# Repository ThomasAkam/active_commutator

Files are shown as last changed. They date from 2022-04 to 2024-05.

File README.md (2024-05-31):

# Active commutator

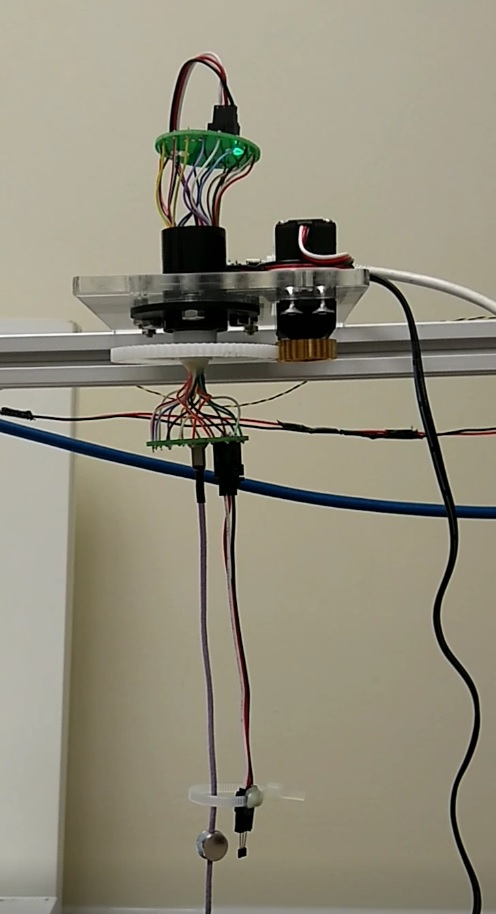
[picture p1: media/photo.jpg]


A simple open source active commutator for Open Ephys / Intan electrophysiology systems.  Uses a hall sensor and magnet to detect rotation of the cable,  a slip ring powered by a continuous rotation servo to correct it, controlled by an Adafruit Trinket M0  running Circuitpython. 

Inspired by earlier designs from [Liberti et al. 2017](https://iopscience.iop.org/article/10.1088/1741-2552/aa6806/meta) and [Fee and Leonardo 2001](https://www.sciencedirect.com/science/article/pii/S0165027001004265).

## Wiring diagram

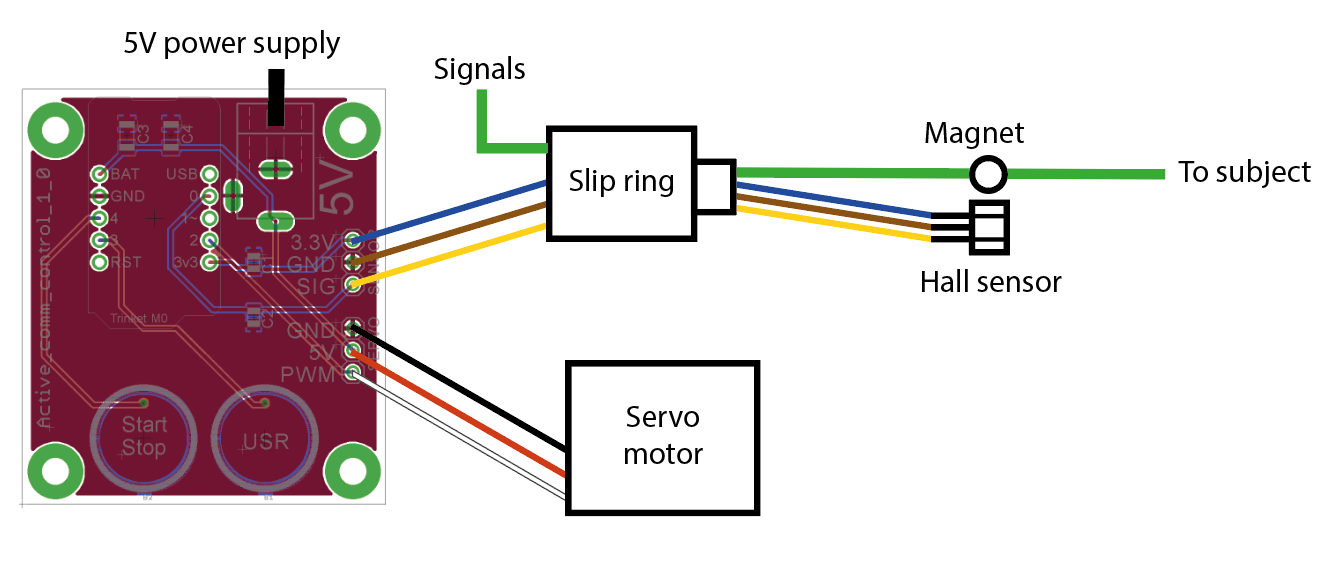
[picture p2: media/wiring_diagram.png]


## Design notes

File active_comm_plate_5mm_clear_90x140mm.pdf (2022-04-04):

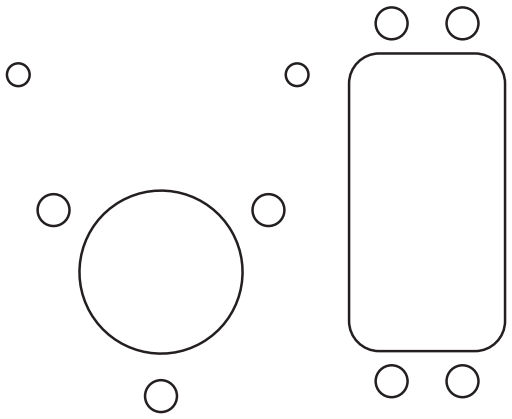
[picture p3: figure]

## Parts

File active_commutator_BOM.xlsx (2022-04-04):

Part | Quantity | Manufacturer | Supplier | Part number | Notes
Mechanical components
Parallax continuous rotation servo (25T/3F spline) | 1 | Parallax | RS | 781-3046 | https://uk.rs-online.com/web/p/servo-motors/7813046
Spur gear mod 0.8, 70 teeth, 6mm bore | 1 | RS | RS | 521-7427 | https://uk.rs-online.com/web/p/spur-gears/5217427/
32P, 24 teeth, 25T/3F Spline, Servo Mount Gear (Metal) | 1 | Servocity | Active Robots | 615306 | https://www.active-robots.com/32p-25t-3f-spline-servo-mount-gears-metal.html
Neodymium magnet 10mm x 1mm | 4 |  | First4Magnets | F307-20 | https://www.first4magnets.com/circular-disc-rod-c34/10mm-dia-x-1mm-thick-n42-neodymium-magnet-0-58kg-pull-p2818|ps_1_936
M4 12mm countersunk screw | 7
M4 Nut | 7
M3 12mm cap head screw | 4
M3 3mm spacer | 4
M3 Nut | 4
Acrylic plate | 1 |  |  |  | Laser cut in 5mm clear acrylic from file active_comm_plate_5mm_clear_90x140mm.dxf
Electrical components
18 wire slip ring | 1 | Senring | Senring | M220-A-18 | https://www.senring.com/capsule-slip-ring/m220.html
Hall sensor 3.3V | 1 | Allegro Microsystems | RS | A1319LUA-5-T | https://uk.rs-online.com/web/p/hall-effect-sensor-ics/8660758/
Phidget Cable 10cm (Molex SL 3 way) | 2 |  | Active Robots |  | https://www.active-robots.com/3003-phidget-cable-10cm.html
active_comm_connector PCB | 2 |  |  |  | Fabricate from Gerbers in folder PCB/active_comm_connector/gerber
active_comm_controller PCB | 1 |  |  |  | Fabricate from Gerbers in folder PCB/active_comm_controller/gerber
5V power supply, 2.1mm barrel plug | 1 | RS | RS | 175-3292 | https://uk.rs-online.com/web/p/ac-dc-adapters/1753292/
Trinket-M0 | 1 | Adafruit | CPC Farnell | SC15313 | Used on active_comm_controller PCB
Pin header 5 way | 2 | Molex | Farnell | 3049532 | Used on active_comm_controller PCB
Receptacle 5 way | 2 | Multicomp | Farnell | 1593461 | Used on active_comm_controller PCB
Pin header 3 way | 1 | Molex | Farnell | 3049527 | Used on active_comm_controller PCB
Capacitor 100nF 0805 | 1 | Multicomp | Farnell | 1759143 | Used on active_comm_controller PCB
Capacitor 4.7nF 0805 | 1 | Multicomp | Farnell | 1759241 | Used on active_comm_controller PCB
Capacitor 220uF 1206 | 2 | Murata | Farnell | 2494472 | Used on active_comm_controller PCB
2.1mm socket | 1 | Lumberg | Farnell | 1217037 | Used on active_comm_controller PCB
Molex SL 3 way header | 3 | Molex | Farnell | 2679892 | Used on active_comm_controller and active_comm_connector PCBs
PZN-12-VV connector | 2 | Omnetics | Genalog |  | Used on active_comm_connector PCB

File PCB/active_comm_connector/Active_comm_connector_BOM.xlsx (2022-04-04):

Part | Value | Device | Package | Description | MF | MPN | OC_FARNELL
PZN-12-VV | - | - | - | Connector | Omnetics | PZN-12-VV

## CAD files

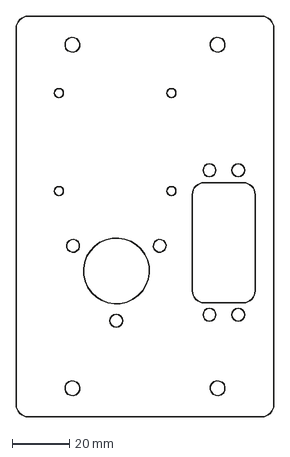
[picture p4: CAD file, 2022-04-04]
active_comm_plate_5mm_clear_90x140mm.dxf
90.0 x 140.0 mm

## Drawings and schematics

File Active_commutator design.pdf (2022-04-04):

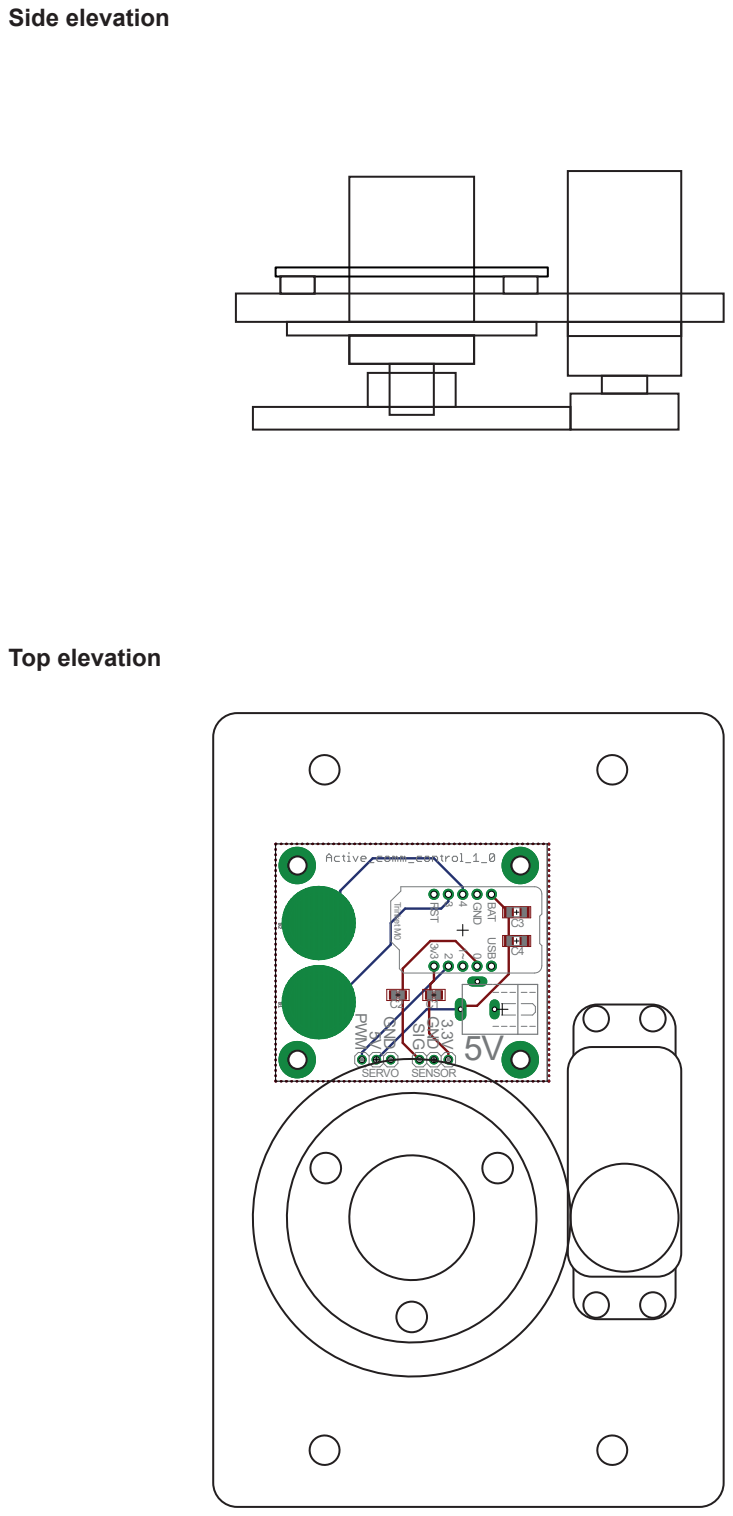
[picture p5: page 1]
Side elevation; GND SIG; GND; Trinket M0; BAT GND; SERVO SENSOR; Top elevation

Start Stop US

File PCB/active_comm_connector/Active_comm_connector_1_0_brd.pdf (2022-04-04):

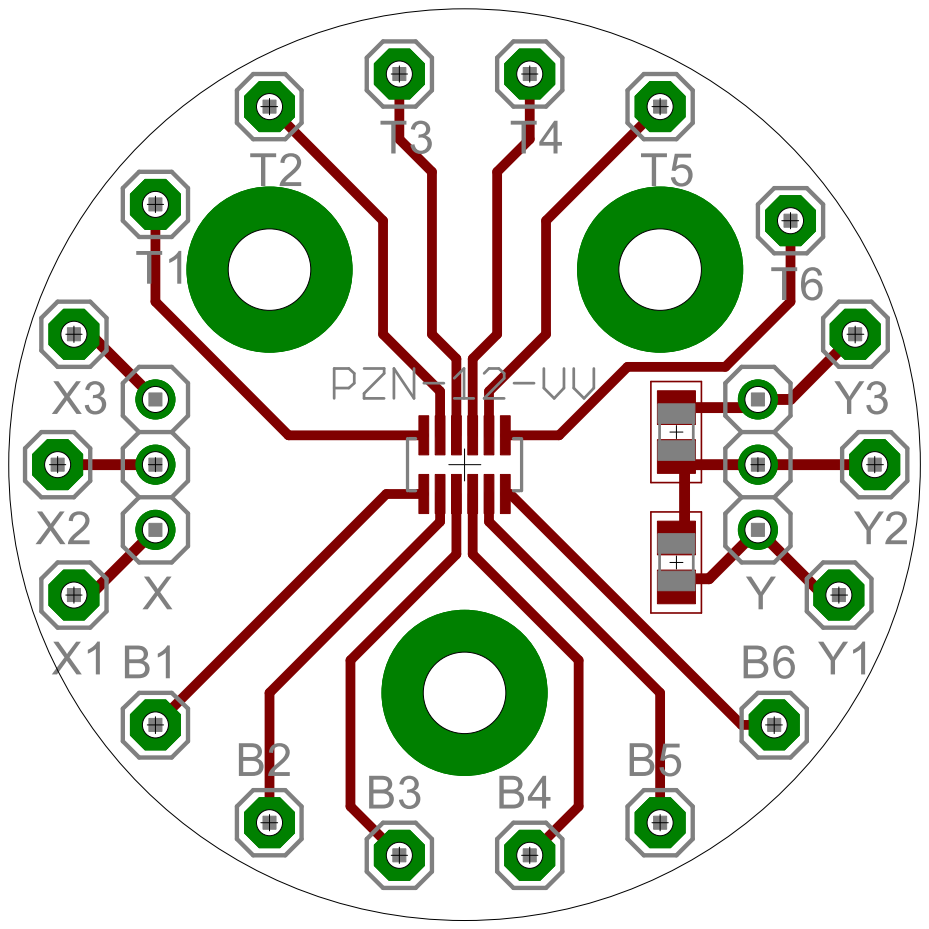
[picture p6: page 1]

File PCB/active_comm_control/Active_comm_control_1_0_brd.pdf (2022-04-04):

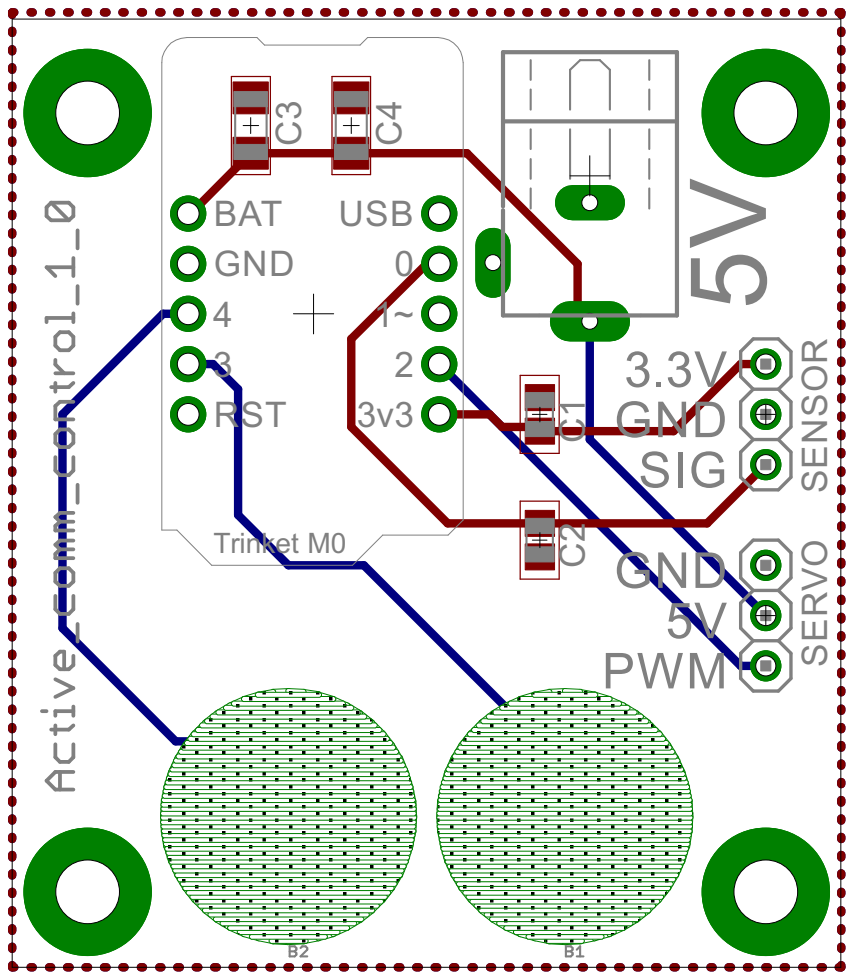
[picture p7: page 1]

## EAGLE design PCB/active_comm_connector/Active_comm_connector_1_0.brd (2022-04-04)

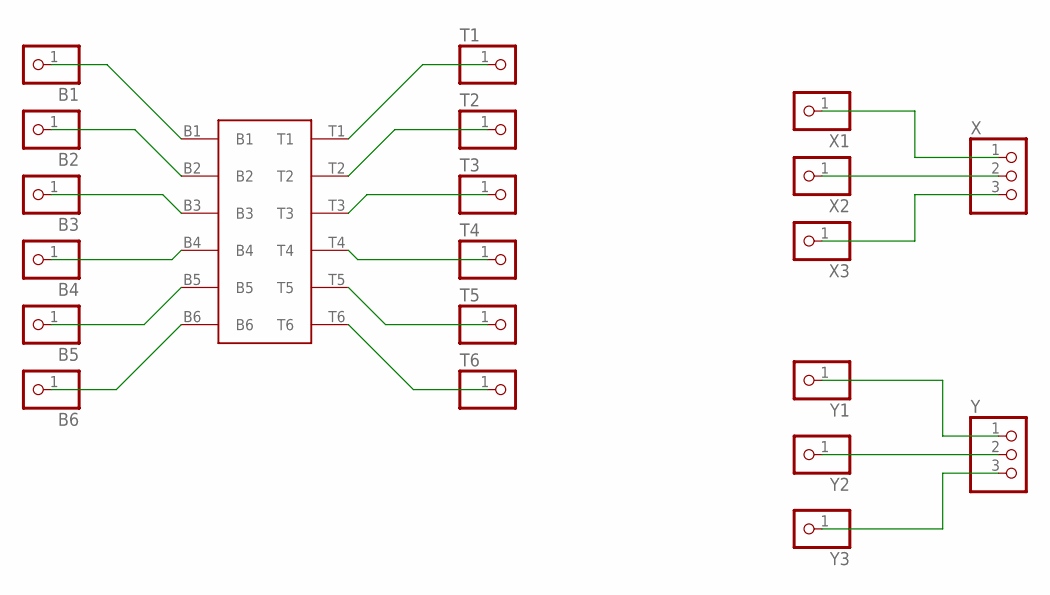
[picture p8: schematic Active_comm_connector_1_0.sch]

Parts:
B1, B2, B3, B4, B5, B6: PINHD-1X1; 1X01
PZN-12-VV: PZN-12-VV; OMNETICS_PZN-12-VV
T1, T2, T3, T4, T5, T6: PINHD-1X1; 1X01
X: PINHD-1X3; 1X03
X1, X2, X3: PINHD-1X1; 1X01
Y: PINHD-1X3; 1X03
Y1, Y2, Y3: PINHD-1X1; 1X01

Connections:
B4: B4.1, PZN-12-VV.B4
unnamed: B1.1, PZN-12-VV.B1
unnamed: B2.1, PZN-12-VV.B2
unnamed: B3.1, PZN-12-VV.B3
unnamed: Y.1, Y1.1
unnamed: B5.1, PZN-12-VV.B5
unnamed: B6.1, PZN-12-VV.B6
unnamed: PZN-12-VV.T1, T1.1
unnamed: PZN-12-VV.T2, T2.1
unnamed: PZN-12-VV.T3, T3.1
unnamed: PZN-12-VV.T4, T4.1
unnamed: PZN-12-VV.T5, T5.1
unnamed: PZN-12-VV.T6, T6.1
unnamed: Y.2, Y2.1
unnamed: Y.3, Y3.1
unnamed: X.2, X2.1
unnamed: X.3, X3.1
XX1: X.1, X1.1

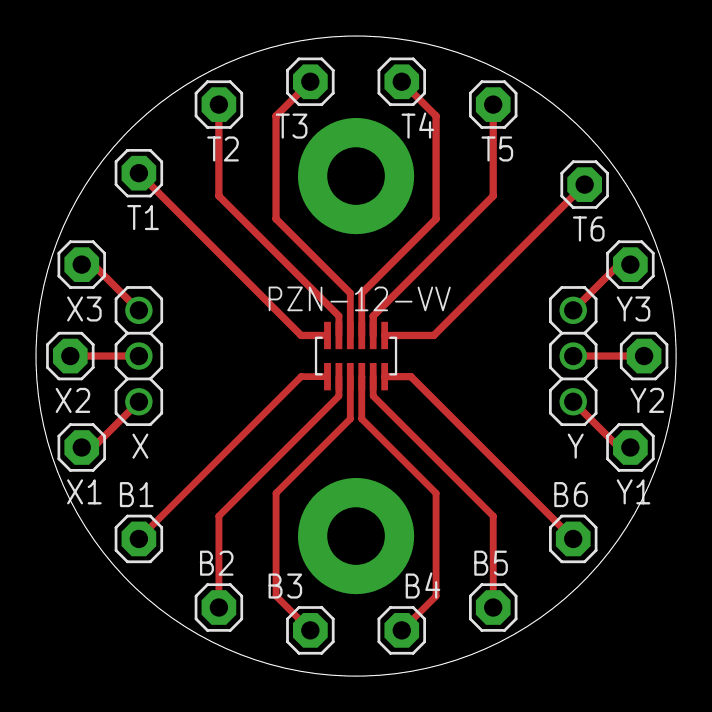
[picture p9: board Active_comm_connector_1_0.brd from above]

Board: 2 copper layers, 35.6 x 35.6 mm, 21 parts (0 on the bottom side), 18 nets.

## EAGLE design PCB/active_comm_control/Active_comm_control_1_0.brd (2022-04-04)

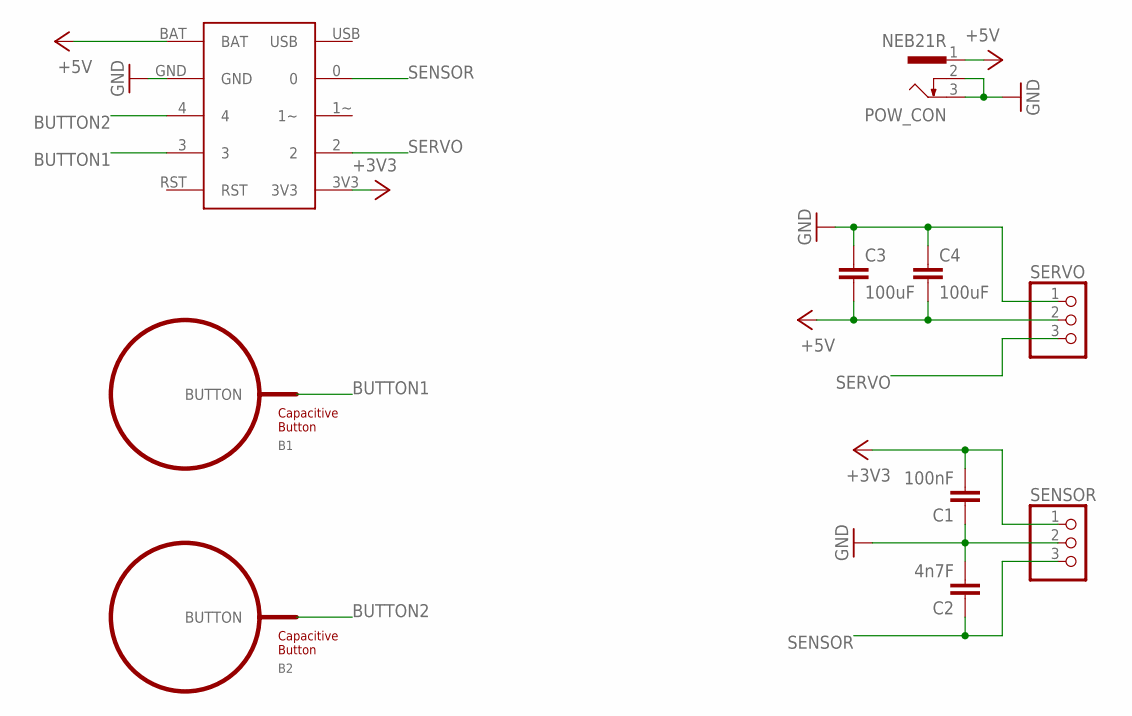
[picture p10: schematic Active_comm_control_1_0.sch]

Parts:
B1, B2: BUTTON_PASSIVE10MM; BUTTON_PASSIVE_10MM
C1: 100nF; C0805
C2: 4n7F; C0805
C3, C4: 100uF; C1206
POW_CON: NEB21R
SENSOR: PINHD-1X3; 1X03
SERVO: PINHD-1X3; 1X03
TRINKET-M0: TRINKET-M0; TRINKET-M0-NO-HOLES

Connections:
+3V3: C1.2, SENSOR.1, TRINKET-M0.3V3
+5V: C3.2, C4.2, POW_CON.1, SERVO.2, TRINKET-M0.BAT
BUTTON1: B1.BUTTON, TRINKET-M0.3
BUTTON2: B2.BUTTON, TRINKET-M0.4
GND: C1.1, C2.2, C3.1, C4.1, POW_CON.2, POW_CON.3, SENSOR.2, SERVO.1, TRINKET-M0.GND
SENSOR: C2.1, SENSOR.3, TRINKET-M0.0
SERVO: SERVO.3, TRINKET-M0.2

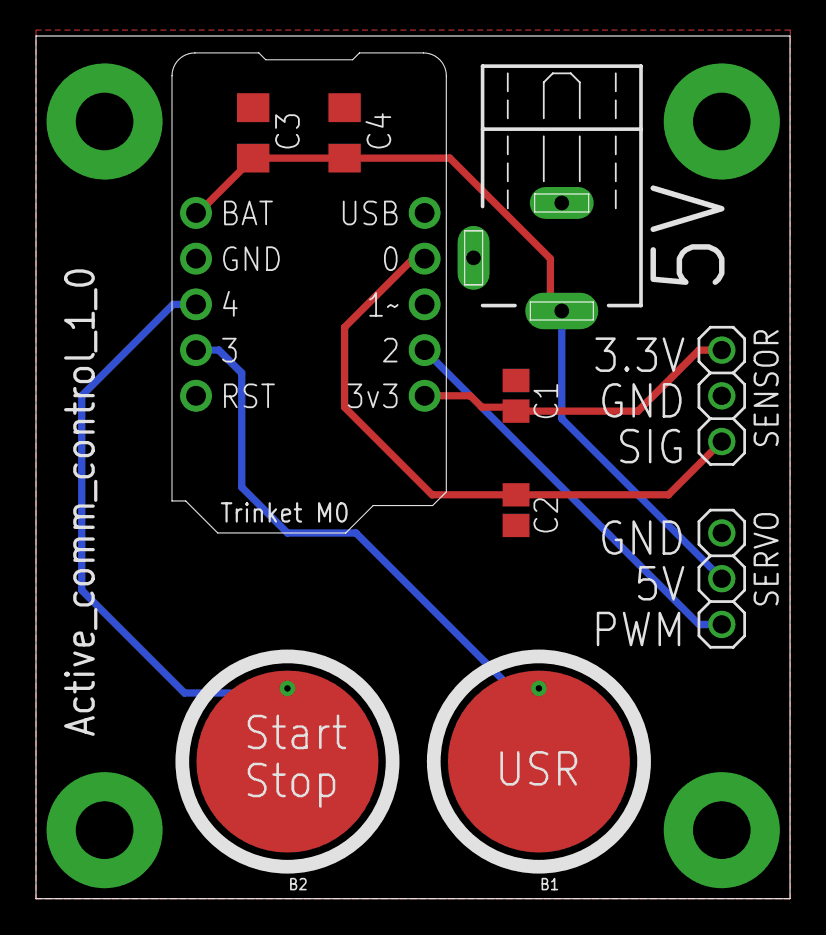
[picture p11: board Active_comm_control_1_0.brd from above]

Board: 2 copper layers, 41.9 x 47.9 mm, 10 parts (0 on the bottom side), 7 nets.

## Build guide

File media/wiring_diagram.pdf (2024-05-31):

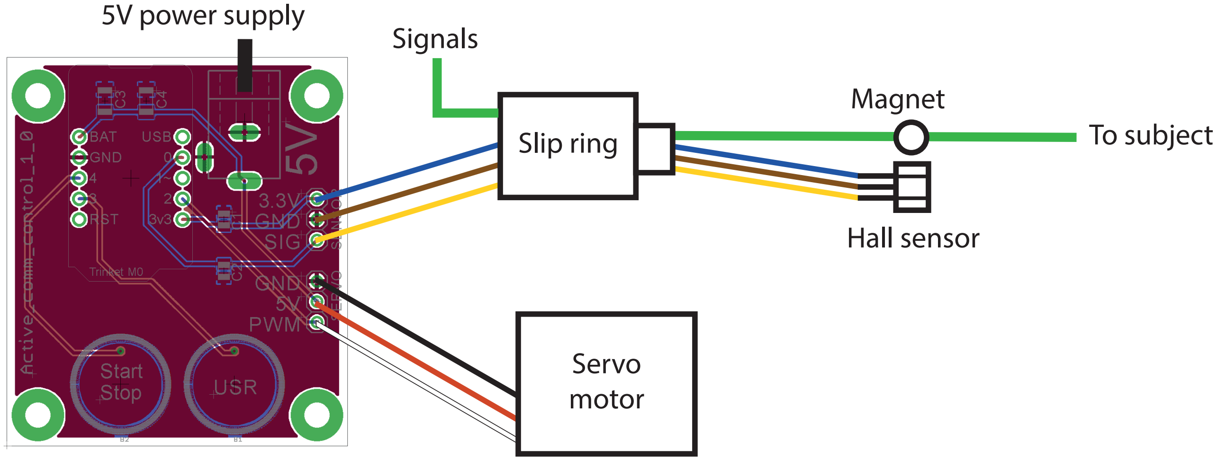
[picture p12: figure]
5V power supply; Servo motor; Hall sensor; Slip ring; Magnet; To subject; Signals

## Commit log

2022-04-04 - Initial commit
    [Active_comm_connector_1_0.GBL, Active_comm_connector_1_0.GBO, Active_comm_connector_1_0.GBS, Active_comm_connector_1_0.GTL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]
2024-05-31 - Updated code to start in "running" state, print info regularly during run, and have different threshold for starting and stopping motion.
2024-05-31 Added wiring diagram to readme

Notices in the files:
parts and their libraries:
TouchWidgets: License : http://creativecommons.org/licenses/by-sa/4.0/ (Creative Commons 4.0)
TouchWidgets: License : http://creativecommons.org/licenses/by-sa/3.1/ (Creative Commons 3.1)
